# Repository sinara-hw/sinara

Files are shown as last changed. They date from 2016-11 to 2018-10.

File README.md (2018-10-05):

This repository is largely depreciated as we now give each piece of hardware its own repository within the [sinara-hw organization](https://github.com/sinara-hw) instead of using this one.

The main exception is issue tracking for Sayma which remains [here](https://github.com/sinara-hw/sinara/issues).

The [meta repository](https://github.com/sinara-hw/meta) is where Sinara management, inter-board design, incubation of new projects, etc. now occur.  Use either the [Main Sinara Wiki](https://github.com/sinara-hw/meta/wiki) or [Meta Issue Tracker](https://github.com/sinara-hw/meta/issues) as appropriate.

All work is licensed under CERN OHL v1.2.

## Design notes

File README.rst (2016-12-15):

Metlino
-------
- ARTIQ_EE/PCB_Metlino is Metlino board housing ARTIQ master FPGA (MCH Tongues 3,4)
- ARTIQ_ALTIUM/PCB_MCH_mordovia is a bare bones clock distribution board (MCH Tongue 2)
- NAT-MCH-Base12-GbE is a commercial MCH that acts as crate controller (MCH Tongue 1)
- these three cards are stacked and shared a common front panel

Sayma
-----
- ARTIQ_EE/PCB_Sayma_AMC is Sayma board with high speed digital components 
- ARTIQ_EE/PCB_Sayma_RTM is Sayma RTM board housing DACs and ADCs
- ARTIQ_ALTIUM/PCB_baikal is Signal/CLK ditribution board for RF-Backplane, slot is eRTM15  (Issue #78)
- ARTIQ_ALTIUM/PCB_mezzanine_clock is DAC clock generation mezzanine
- ARTIQ_ALTIUM/PCB_mezzanine_clock_template is simple test board and template for more complex clock mezzanines 
- ARTIQ_ALTIUM/PCB_mezzanine_analog_template is simple test board and template for more complex analog mezzanines 
- ARTIQ_ALTIUM/PCB_mezzanine_analog_allaki is analog mezzanine for base band output and DC-100 kHz input 

Note
----
- ARTIQ_EE folder is for designs made with the Mentor Graphics Xpedition Enterprise CAD tool.
- ARTIQ_ALTIUM folder is for designs made with Altium Designer CAD tool.
- See Issue 21_ for a list of hardware that comprises a Sinara system. 
.. _21: https://github.com/m-labs/sinara/issues/21

Modules to add to git
---------------------
- let ARTIQ_xx/BP_AMC/PCB_BP_AMC be microTCA.4 AMC backplane (no schematic currently available) 
- let ARTIQ_xx/BP_RTM/PCB_BP_RTM_RF be microTCA.4 RF backplane (no schematic currently available)

--------------
The hardware designs for the Sinara device family are distributed under the
CERN Open Hardware Licence v1.2.

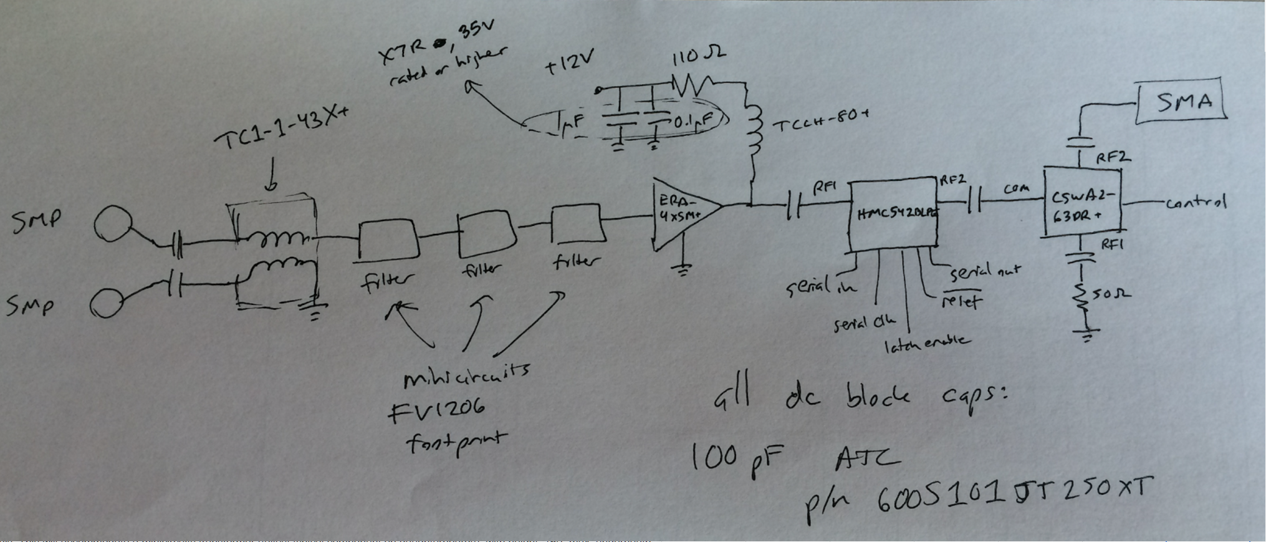
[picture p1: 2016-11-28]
ARTIQ_ALTIUM/Sayma_AFEs/BaseMod/Docs/paper_schematic.png

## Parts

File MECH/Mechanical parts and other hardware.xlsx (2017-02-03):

 | MFR |  | Sayma AMC | Sayma RTM | Metlino | Kasli | VHDCI BB | BNC IO | SMA IO | RJ45IO | DAC
LED lightpipes | BIVAR | PLPC1-100 | 6
AMC panel | Schroff | 21850070 | 1 | 1
MTCA panel | Schroff | 21850071 |  |  | 1
3U panel |  |  |  |  |  | 20848664 | 20848664 | 20849107 | 20848664 | 20848664 | 20848670
SMA isolation washer | http://www.rf-microwave.com/datasheets/603_Huber-Suhner_77-Z-0-0-8_01.pdf
AMC/Metlino heatsink | AAVID | 342947 (http://www.aavid.com/products/bga/342947) | 1 |  | 1
RTM/Kasli heatsink
RTM standoff 9mm M2.5 | RAF ELECTRONIC HARDWARE (http://pl.farnell.com/raf-electronic-hardware/m1256-2545-al/spacer-standoff-hex-aluminium/dp/1873361) | M1256-2545-AL (http://pl.farnell.com/raf-electronic-hardware/m1256-2545-al/spacer-standoff-hex-aluminium/dp/1873361) |  | 20
RTM standoff screw M2.5 6mm | DURATOOL (http://pl.farnell.com/duratool/m2-56-prstmcz100/screw-pozi-pan-steel-bzp-m2-5x6/dp/1420388) | M2.56 PRSTMCZ100- (http://pl.farnell.com/duratool/m2-56-prstmcz100/screw-pozi-pan-steel-bzp-m2-5x6/dp/1420388) |  | 40
SATA cable 1m |  |  | 1
SFP plug |  |  | 1
ATX supply |  |  |  |  | 1
IDC cable 30 wires |  |  |  |  |  |  | 1 | 1 | 1 | 2 | 1
IDC plug 30 contacts |  |  |  |  |  |  | 2 | 2 | 2 | 4 | 2
VHDCI cable |  |  |  |  | 2
FMC EMC strip for AMC |  |  | 1
12V wall wart |  |  |  |  |  | 1 | 1
SMA assembly distance |  |  |  | 8 | 2
SMP-SMP jack 6.45mm | Radiall | R222 705 000 |  | 48 |  |  |  |  |  |  |  | 7.6$@100
SMP-SMP jack 6.45mm | Rosenberger | 19K101-K00L5 |  |  |  |  |  |  |  |  |  | 8.09$@100
SMP-SMP jack 6.40mm | TE | 1056700-1
SMP-SMP jack 6.46 | Molex | 73415-4295 / 73415-4293
SMP-SMP jack 6.46 | Amphenol | 1290-4008 (http://www.digikey.com/product-detail/en/amphenol-sv-microwave/1290-4008/1290-4008-ND/6050843) |  |  |  |  |  |  |  |  |  | 15.8$@100
SMP-SMP jack 6.45 | Telegarthener | J01392A0001

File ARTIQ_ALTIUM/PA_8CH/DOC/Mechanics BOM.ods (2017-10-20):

Item name | description | quantity | remarks
20860-606 | modified Schroff enclosure | 1
PMD1207PTV1AF (https://www.tme.eu/pl/katalog/?art=PMD1207PTV1AF) | fan 70x70x25 | 5 | fan holes -> 5mm
STP5X10 (https://www.tme.eu/pl/details/stp5x10/elementy-montazowe/) | fan screw | 20
 | user module fixing | 1
 | mainboard platform | 1
 | RF module fixing | 1
7662686 | IEC inlet Schrack | 1
Threaded Strip M3, 30821-589, Pentair Schroff | threaded insert | 2
HLG-185H-30A (https://www.tme.eu/pl/details/hlg-185h-30a/zasilacze-do-led/mean-well/) | power supply module 30V/6A

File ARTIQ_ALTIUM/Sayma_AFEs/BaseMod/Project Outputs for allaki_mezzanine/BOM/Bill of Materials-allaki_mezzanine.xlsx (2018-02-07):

Comment | Description | Designator | Footprint | Manufacturer | Manufacturer Part Number | Manufacturer1 ComponentHeight | Manufacturer1 Example | Manufacturer1 Part Number | Part Description | Part Number | Quantity
100nF | Non-polarised capacitor | C1A, C1B, C5A, C5B, C6A, C6B, C22A, C22B, C35A, C35B, C40A, C40B, C41A, C41B, C43, C54, C57A, C57B, C58A, C58B, C59A, C59B, C60A, C60B | CAPC1005X55N | GENERIC | CC0402_100NF_16V_10%_X5R, CC0402_100NF_16V_10%_X5R, CC0402_100NF_16V_10%_X5R, CC0402_100NF_16V_10%_X5R, CC0402_100NF_16V_10%_X5R, CC0402_100NF_16V_10%_X5R, CC0402_100NF_16V_10%_X7R, CC0402_100NF_16V_10%_X7R, CC0402_100NF_16V_10%_X7R, CC0402_100NF_16V_10%_X7R, CC0402_100NF_16V_10%_X7R, CC0402_100NF_16V_10%_X7R, CC0402_100NF_16V_10%_X7R, CC0402_100NF_16V_10%_X7R, CC0402_100NF_16V_10%_X5R, CC0402_100NF_16V_10%_X5R, CC0402_100NF_16V_10%_X5R, CC0402_100NF_16V_10%_X5R, CC0402_100NF_16V_10%_X5R, CC0402_100NF_16V_10%_X5R, CC0402_100NF_16V_10%_X5R, CC0402_100NF_16V_10%_X5R, CC0402_100NF_16V_10%_X5R, CC0402_100NF_16V_10%_X5R | 0.55mm | MURATA | GRM155R61C104KA88D, GRM155R61C104KA88D, GRM155R61C104KA88D, GRM155R61C104KA88D, GRM155R61C104KA88D, GRM155R61C104KA88D, GRM155R71C104KA88D, GRM155R71C104KA88D, GRM155R71C104KA88D, GRM155R71C104KA88D, GRM155R71C104KA88D, GRM155R71C104KA88D, GRM155R71C104KA88D, GRM155R71C104KA88D, GRM155R61C104KA88D, GRM155R61C104KA88D, GRM155R61C104KA88D, GRM155R61C104KA88D, GRM155R61C104KA88D, GRM155R61C104KA88D, GRM155R61C104KA88D, GRM155R61C104KA88D, GRM155R61C104KA88D, GRM155R61C104KA88D | SMD Multilayer Chip Ceramic Capacitor | CC0402_100NF_16V_10%_X5R, CC0402_100NF_16V_10%_X5R, CC0402_100NF_16V_10%_X5R, CC0402_100NF_16V_10%_X5R, CC0402_100NF_16V_10%_X5R, CC0402_100NF_16V_10%_X5R, CC0402_100NF_16V_10%_X7R, CC0402_100NF_16V_10%_X7R, CC0402_100NF_16V_10%_X7R, CC0402_100NF_16V_10%_X7R, CC0402_100NF_16V_10%_X7R, CC0402_100NF_16V_10%_X7R, CC0402_100NF_16V_10%_X7R, CC0402_100NF_16V_10%_X7R, CC0402_100NF_16V_10%_X5R, CC0402_100NF_16V_10%_X5R, CC0402_100NF_16V_10%_X5R, CC0402_100NF_16V_10%_X5R, CC0402_100NF_16V_10%_X5R, CC0402_100NF_16V_10%_X5R, CC0402_100NF_16V_10%_X5R, CC0402_100NF_16V_10%_X5R, CC0402_100NF_16V_10%_X5R, CC0402_100NF_16V_10%_X5R | 24
10uF | Non-polarised capacitor | C2A, C2B, C7A, C7B, C11, C70 | CAPC1608X87N | GENERIC | CC0603_10uF_6.3V_20%_X5R | 0.95mm | KEMET | C0603C106M9PAC | SMD Multilayer Chip Ceramic Capacitor | CC0603_10UF_6.3V_20%_X5R | 6
1nF | Non-polarised capacitor | C3A, C3B, C8A, C8B, C23A, C23B | CAPC1005X55N | GENERIC | CC0402_1NF_50V_10%_X7R | 0.55mm | PHYCOMP | 223858715623 | SMD Multilayer Chip Ceramic Capacitor | CC0402_1NF_50V_10%_X7R | 6
10pF | Non-polarised capacitor | C4A, C4B, C63A, C63B | CAPC1608X87N | GENERIC | CC0603_10PF_50V_5%_NP0 | 0.87mm | PHYCOMP | 223886715109 | SMD Multilayer Chip Ceramic Capacitor | CC0603_10PF_50V_5%_NP0 | 4
18pF | Non-polarised capacitor | C9A, C9B, C33A, C33B | CAPC1005X55N | GENERIC | CC0402_18PF_50V_5%_C0G | 0.55mm | KEMET | C0402C180J5GACTU | SMD Multilayer Chip Ceramic Capacitor | CC0402_18PF_50V_5%_C0G | 4
10pF | Non-polarised capacitor | C10, C32 | CAPC1005X55N | GENERIC | CC0402_10PF_50V_5%_C0G | 0.55mm | KEMET | C0402C100J5GACTU | SMD Multilayer Chip Ceramic Capacitor | CC0402_10PF_50V_5%_C0G | 2
1uF | Non-polarised capacitor | C12A, C12B | CAPC2012X140N | GENERIC | CC0805_1UF_35V_20%_X7R | 1.35mm | TAIYO YUDEN | GMK212B7105MG-T | SMD Multilayer Chip Ceramic Capacitor | CC0805_1UF_35V_20%_X7R | 2
100nF | Non-polarised capacitor | C13A, C13B | CAPC1608X87N | GENERIC | CC0603_100NF_50V_10%_X7R | 0.87mm | PHYCOMP | 223858615649 | SMD Multilayer Chip Ceramic Capacitor | CC0603_100NF_50V_10%_X7R | 2
10nF | Non-polarised capacitor | C14A, C14B, C15A, C15B, C16A, C16B, C17A, C17B, C18A, C18B, C19A, C19B, C20A, C20B, C28A, C28B, C29A, C29B, C36A, C36B, C37A, C37B, C46A, C46B, C47A, C47B, C49A, C49B, C50A, C50B, C51, C52, C55A, C55B, C56A, C56B, C64, C65, C66, C67, C68, C69 | CAPC1005X55N | GENERIC | CC0402_10NF_16V_10%_X7R | 0.55mm | PHYCOMP | 223878715636 | SMD Multilayer Chip Ceramic Capacitor | CC0402_10NF_16V_10%_X7R | 42
10uF | Non-polarised capacitor | C21A, C21B, C39A, C39B | CAPC1608X80N | GENERIC | CC0603_10UF_16V_20%_X5R | 0.8mm | MURATA | GRM188R61C106MA73D | SMD Multilayer Chip Ceramic Capacitor | CC0603_10UF_16V_20%_X5R | 4
100pF | Non-polarised capacitor | C24A, C24B, C30A, C30B, C38A, C38B, C45A, C45B, C61A, C61B, C62A, C62B | CAPC1005X55N | GENERIC | CC0402_100PF_50V_5%_C0G | 0.55mm | KEMET | C0402C101J5GACTU | SMD Multilayer Chip Ceramic Capacitor | CC0402_100PF_50V_5%_C0G | 12
4.7uF | Non-polarised capacitor | C25, C26, C71, C72 | CAPC1709X95N | GENERIC | CC0603_4.7UF_16V_10%_X5R | 0.95mm | TAIYO YUDEN | EMK107ABJ475KA-T | SMD Multilayer Chip Ceramic Capacitor | CC0603_4.7UF_16V_10%_X5R | 4
2.2uF | Non-polarised capacitor | C27, C53 | CAPC1608X90N | GENERIC | CC0603_2.2UF_10V_20%_X7R | 0.9mm | TAIYO YUDEN | LMK107B7225MA-T | SMD Multilayer Chip Ceramic Capacitor | CC0603_2.2UF_10V_20%_X7R | 2
180pF | Non-polarised capacitor | C31A, C31B | CAPC3216X140N | GENERIC | CC1206_180PF_50V_5%_NP0 | 1.7mm | VISHAY VITRAMON | VJ1206A181JXAAT | SMD Multilayer Chip Ceramic Capacitor | CC1206_180PF_50V_5%_NP0 | 2
10uF | Polarised capacitor | C34A, C34B, C42A, C42B | CAPMP3216X180N | AVX | TCJA106M016R0200 |  |  |  | ESR 0R200 Tantalum Solid Electrolytic Chip Capacitor with Conductive Polymer Electrode | CTE3216-18_10UF_16V_20%_AVX_TCJ | 4
0.5pF | CAP 0.5pF 10V ±0.1pF 0402 (1005 Metric) Thickness 0.6mm SMD | C44A, C44B, C48A, C48B | CAPC0402(1005)60_M |  |  |  |  |  |  |  | 4
BAV199 | Serial Diode | D1A, D1B, D2A, D2B, D3A, D3B, D4A, D4B | SOT95P240X110-3N | NXP SEMICONDUCTORS | BAV199 |  |  |  | Low-Leakage Double Diode | BAV199 | 8
1PS76SB10 | Schottky Diode | D5, D6 | SOD2512X110N | NXP SEMICONDUCTORS | 1PS76SB10 |  |  |  | Schottky Barrier Single Diode | 1PS76SB10 | 2
DC to 3000MHz | 50 Ohm DC to 3000MHz Low Pass Filter | FL2A, FL2B, FL3A, FL3B, FL4A, FL4B | FIL_MINI-CIRCUITS_FV1206 | MINI-CIRCUITS | LFCN-3000+ |  |  |  | 50 Ohm Low Pass Filter | FIL_MINI-CIRCUITS_LFCN-3000+ | 6
ADT7420UCPZ-R2 | ±0.25°C Accurate, 16-Bit Digital I2C Temperature Sensor | IC1 | QFN65P400X400X80-17N-S270 | ANALOG DEVICES | ADT7420UCPZ-R2 |  |  |  | -20° to +105°C ±0.25°C Accurate, 16-Bit Digital I2C Temperature Sensor | ADT7420UCPZ-R2 | 1
ADA4927-1YCPZ-R2 | Ultralow Distortion Current Feedback Differential ADC Driver | IC2A, IC2B | QFN50P300X300X100-17N-S145 | ANALOG DEVICES | ADA4927-1YCPZ-R2 |  |  |  | Ultralow Distortion Current Feedback Differential ADC Driver | ADA4927-1YCPZ-R2 | 2
HMC542BLP4E | 0.5dB LSB GaAs MMIC 6-bit Digital Serial Control Attenuator, DC - 4GHz | IC3A, IC3B | QFN50P400X400X100-25N-S295 | HITTITE MICROWAVE CORP | HMC542BLP4E |  |  |  | 0.5dB LSB GaAs MMIC 6-bit Digital Serial Control Attenuator, DC to 4GHz | HMC542BLP4E | 2
YAT-12+ | DC to 18GHz, 2W, 50 Ohm, 4dB Attenuator | IC4A, IC4B | MINI-CIRCUITS_MC1630 | MINI-CIRCUITS | YAT-12+ |  |  |  | DC to 18GHz, 2W, 50 Ohms, 12dB Attenuator | YAT-12+ | 2
ERA-4XSM+ | DC-4GHz Monolithic Amplifier | IC5A, IC5B | MINI-CIRCUITS_WW107 | MINI-CIRCUITS | ERA-4XSM+ |  |  |  | DC-4GHz Monolithic Amplifier | ERA-4XSM+ | 2
AD8253ARMZ | 10MHz, 20V/us, G= 1, 10, 100, 1000 iCMOS Programmable Gain Instrumentation Amplifier | IC6A, IC6B | SOP50P490X110-10N | ANALOG DEVICES | AD8253ARMZ |  |  |  | 10MHz, 20V/us, G= 1, 10, 100, 1000 iCMOS Programmable Gain Instrumentation Amplifier | AD8253ARMZ | 2
HMC349ALP4CE | DC-4GHz High Isolation SPDT Non-Reflective Switch | IC7A, IC7B | QFN65P400X400X100-17N-S255 | ANALOG DEVICES | HMC349ALP4CE |  |  |  | DC-4GHz High Isolation SPDT Non-Reflective Switch | HMC349ALP4CE | 2
LT3045EDD#PBF | 20V, 500mA, Ultralow Noise, Ultrahigh PSRR Linear Regulator | IC8, IC10 | SON50P300X300X80-11N-R175X248 | LINEAR TECHNOLOGY | LT3045EDD#PBF |  |  |  | 20V, 500mA, Ultralow Noise, Ultrahigh PSRR Linear Regulator | LT3045EDD#PBF | 2
ADP7182AUJZ-5.0-R7 | –5V, 200 mA, Low Noise, Linear Regulator | IC9 | SOT95P280X90-5N | ANALOG DEVICES | ADP7182AUJZ-5.0-R7 |  |  |  | –5V, -200mA, Low Noise, Linear Regulator | ADP7182AUJZ-5.0-R7 | 1
24AA02E48T-I/OT | 1.7V-5.5V, 2K I2C Serial EEPROM With EUI-48 Node Identity | IC14 | SOT95P280X145-5N | MICROCHIP TECHNOLOGY | 24AA02E48T-I/OT |  |  |  | 1.7V-5.5V, 2K I2C Serial EEPROM With EUI-48 Node Identity | 24AA02E48T-I/OT | 1
SMP | 50 Ohms, SMP Surface/THT Mount Plug, Limited Detent | J1, J3, J4, J6, J14, J15 | AMPHENOL_SMP-MSLD-PCT-10 | AMPHENOL | SMP-MSLD-PCT-10 |  |  |  | 50 Ohms, SMP Surface Mount Plug, Limited Detent | AMPHENOL_SMP-MSLD-PCT-10 | 6
SMA | RiSMA 50 Ohms Right Angle PCB Jack | J2, J5 | Telegartner_J01151A0921 | Telegartner | J01151A0921 |  |  |  | SMA 50 Ohms Right Angle PCB Jack | Telegartner_J01151A0921 | 2
SMP |  | J7, J9, J10, J12 | MOLEX_85305-0232 | MOLEX | 85305-0232 |  |  |  | 50 Ohms, SMP Surface Mount Plug, Limited Detent | MOLEX_85305-0232 | 4
SMA |  | J8, J11 | TELEGARTNER_J01151A0451 | TELEGARTNER | J01151A0451 |  |  |  | SMA 50 ohms Edge Mount Bulkhead Jack Receptacle | TELEGARTNER_J01151A0451 | 2
Familly | 40 Contacts, Pitch 0.635mm, Razor Beam LSS Vertical High Speed Hermaphroditic Strip (Lead Style 7.49mm) | J13 | SAMTEC_LSS-120-02-L-DV-A | SAMTEC | LSS-120-02-L-DV-A |  |  |  | 40 Contacts, Pitch 0.635mm, Razor Beam LSS Vertical High Speed Hermaphroditic Strip (Lead Style 5.49mm) | SAMTEC_LSS-120-02-L-DV-A | 1
0.5uH@200mA | 50 Ohms, 50 to 8200 MHz RF Choke | L1A, L1B | IND_MINI-CIRCUITS_GU1604 | MINI-CIRCUITS | TCCH-80+ |  |  |  | 50 Ohms, 50 to 8200 MHz RF Choke | IND_MINI-CIRCUITS_TCCH-80+ | 2
390R@100MHz | Inductor | L2A, L2B, L3A, L3B, L4, L5A, L5B, L6A, L6B, L7A, L7B, L8A, L8B, L9, L10 | INDC1608X95N | TDK | MPZ1608R391A |  |  |  | SMT Chip Bead for Power Line | IND0603_TDK_MPZ1608R391A | 15
698 | Resistor - 0.1% | R1A, R1B, R9A, R9B, R13A, R13B, R22A, R22B | RESC1608X55N | GENERIC | R0603_698R_0.1%_0.063W_10PPM | 0.5mm | TYCO HOLSWORTHY | RN73C1J698RBTDF | Thin Film Chip Resistor | R0603_698R_0.1%_0.063W_10PPM | 8
0 | Resistor | R2A, R2B, R3A, R3B, R4A, R4B, R7A, R7B, R10A, R10B, R14A, R14B, R15A, R15B, R21A, R21B, R24A, R24B, R35A, R35B, R38A, R38B, R43A, R43B, R44A, R44B, R45A, R45B, R46A, R46B, R47A, R47B, R48A, R48B, R49A, R49B, R50A, R50B, R51A, R51B, R52A, R52B, R53A, R53B, R54A, R54B, R55A, R55B, R56A, R56B, R57A, R57B, R58A, R58B, R59A, R59B, R65A, R65B, R66A, R66B, R67A, R67B | RESC1005X40N | GENERIC | R0402_0R_JUMPER | 0.4mm | YAGEO PHYCOMP | 232270591001L | 1A (0.05R Max DC Resistance) Zero Ohm Jumper | R0402_0R_JUMPER | 62
100 | Resistor - 1% | R5A, R5B | RESC3216X65N | GENERIC | R1206_100R_1%_0.25W_100PPM | 0.65mm | NIC COMPONENT | NRC12F4700TRF | General Purpose Thick Film Chip Resistor | R1206_100R_1%_0.25W_100PPM | 2
DNP | Resistor, Resistor, Resistor, Resistor, Resistor, Resistor, Resistor, Resistor, Resistor - 1%, Resistor - 1% | R6A, R6B, R8A, R8B, R11A, R11B, R12A, R12B, R16A, R16B | RESC1005X40N | GENERIC | R0402_0R_JUMPER, R0402_0R_JUMPER, R0402_0R_JUMPER, R0402_0R_JUMPER, R0402_0R_JUMPER, R0402_0R_JUMPER, R0402_0R_JUMPER, R0402_0R_JUMPER, R0402_56R_1%_0.0625W_100PPM, R0402_56R_1%_0.0625W_100PPM | 0.4mm | YAGEO PHYCOMP | 232270591001L, 232270591001L, 232270591001L, 232270591001L, 232270591001L, 232270591001L, 232270591001L, 232270591001L, 232270675609L, 232270675609L | 1A (0.05R Max DC Resistance) Zero Ohm Jumper, 1A (0.05R Max DC Resistance) Zero Ohm Jumper, 1A (0.05R Max DC Resistance) Zero Ohm Jumper, 1A (0.05R Max DC Resistance) Zero Ohm Jumper, 1A (0.05R Max DC Resistance) Zero Ohm Jumper, 1A (0.05R Max DC Resistance) Zero Ohm Jumper, 1A (0.05R Max DC Resistance) Zero Ohm Jumper, 1A (0.05R Max DC Resistance) Zero Ohm Jumper, General Purpose Thick Film Chip Resistor, General Purpose Thick Film Chip Resistor | R0402_0R_JUMPER, R0402_0R_JUMPER, R0402_0R_JUMPER, R0402_0R_JUMPER, R0402_0R_JUMPER, R0402_0R_JUMPER, R0402_0R_JUMPER, R0402_0R_JUMPER, R0402_56R_1%_0.0625W_100PPM, R0402_56R_1%_0.0625W_100PPM | 10
100 | Resistor - 1% | R17 | RESC1005X40N | GENERIC | R0402_100R_1%_0.0625W_100PPM | 0.4mm | YAGEO PHYCOMP | 232270671001L | General Purpose Thick Film Chip Resistor | R0402_100R_1%_0.0625W_100PPM | 1
100 | Resistor - 1% | R18A, R18B, R19A, R19B | RESC0603X28N | GENERIC | R0201_100R_1%_0.05W_200PPM | 0.27mm | VISHAY | CRCW0201100RFNED | Thick Film Chip Resistor | R0201_100R_1%_0.05W_200PPM | 4
4k7 | Resistor - 1% | R20A, R20B, R23A, R23B | RESC1005X40N | GENERIC | R0402_4K7_1%_0.0625W_100PPM | 0.4mm | YAGEO PHYCOMP | 232270674702L | General Purpose Thick Film Chip Resistor | R0402_4K7_1%_0.0625W_100PPM | 4
1k4 | Resistor - 0.1% | R25A, R25B | RESC1608X55N | GENERIC | R0603_1K4_0.1%_0.063W_10PPM | 0.5mm | TYCO HOLSWORTHY | RN73C1J1K4BTDF | Thin Film Chip Resistor | R0603_1K4_0.1%_0.063W_10PPM | 2
1k | Resistor - 1% | R26A, R26B, R27A, R27B, R31A, R31B, R41A, R41B | RESC1005X40N | GENERIC | R0402_1K_1%_0.0625W_100PPM | 0.4mm | YAGEO PHYCOMP | 232270671002L | General Purpose Thick Film Chip Resistor | R0402_1K_1%_0.0625W_100PPM | 8
845 | Resistor - 0.1% | R28A, R28B | RESC1608X55N | GENERIC | R0603_845R_0.1%_0.063W_10PPM | 0.5mm | TYCO HOLSWORTHY | RN73C1J845RBTDF | Thin Film Chip Resistor | R0603_845R_0.1%_0.063W_10PPM | 2
3k24 | Resistor - 0.1% | R29A, R29B | RESC1608X55N | GENERIC | R0603_3K24_0.1%_0.063W_10PPM | 0.5mm | TYCO HOLSWORTHY | RN73C1J3K24BTDF | Thin Film Chip Resistor | R0603_3K24_0.1%_0.063W_10PPM | 2
13k | Resistor - 1% | R30A, R30B | RESC1005X40N | GENERIC | R0402_13K_1%_0.0625W_100PPM | 0.4mm | YAGEO PHYCOMP | 232270671303L | General Purpose Thick Film Chip Resistor | R0402_13K_1%_0.0625W_100PPM | 2
10k | Resistor - 1% | R32A, R32B | RESC1005X40N | GENERIC | R0402_10K_1%_0.0625W_100PPM | 0.4mm | YAGEO PHYCOMP | 232270671003L | General Purpose Thick Film Chip Resistor | R0402_10K_1%_0.0625W_100PPM | 2
1k5 | Resistor - 0.1% | R33A, R33B, R36A, R36B | RESC1608X55N | GENERIC | R0603_1K5_0.1%_0.063W_10PPM | 0.5mm | TYCO HOLSWORTHY | RN73C1J1K5BTDF | Thin Film Chip Resistor | R0603_1K5_0.1%_0.063W_10PPM | 4
100k | Resistor - 0.1% | R34A, R34B, R37A, R37B | RESC1005X35N | GENERIC | R0402_100K_0.1%_0.063W_25PPM | 0.35mm | TE CONNECTIVITY | CPF0402B100KE1 | Thin Film Precision Resistor | R0402_100K_0.1%_0.063W_25PPM | 4
49k9 | Resistor - 0.1% | R39 | RESC1608X55N | GENERIC | R0603_49K9_0.1%_0.063W_10PPM | 0.5mm | TYCO HOLSWORTHY | RN73C1J49K9BTDF | Thin Film Chip Resistor | R0603_49K9_0.1%_0.063W_10PPM | 1
49R9 | Resistor - 1% | R40A, R40B, R42A, R42B | RESC1005X40N | GENERIC | R0402_49R9_1%_0.0625W_100PPM | 0.4mm | YAGEO PHYCOMP | 232270674999L or RC0402FR-0749R9L | General Purpose Thick Film Chip Resistor | R0402_49R9_1%_0.0625W_100PPM | 4
115k | Resistor - 0.1% | R60 | RESC1608X55N | GENERIC | R0603_115K_0.1%_0.063W_10PPM | 0.5mm | TYCO HOLSWORTHY | RN73C1J115KBTDF | Thin Film Chip Resistor | R0603_115K_0.1%_0.063W_10PPM | 1
100k | Resistor - 1% | R61, R62, R63, R64 | RESC1005X40N | GENERIC | R0402_100K_1%_0.0625W_100PPM | 0.4mm | YAGEO PHYCOMP | 232270671004L | General Purpose Thick Film Chip Resistor | R0402_100K_1%_0.0625W_100PPM | 4
3k3 | Resistor - 1% | R68A, R68B | RESC1005X40N | GENERIC | R0402_3K3_1%_0.0625W_100PPM | 0.4mm | YAGEO PHYCOMP | 232270673302L | General Purpose Thick Film Chip Resistor | R0402_3K3_1%_0.0625W_100PPM | 2
1:2 | 50 OHMS 10 to 4000 MHz RF Transformer | TR1A, TR1B | XFMR_MINI-CIRCUITS_DB1627 | MINI-CIRCUITS | TCM2-43X+ |  |  |  | 50 Ohms 10 to 4000MHz RF Transformer | XFMR_MINI-CIRCUITS_TCM2-43X+ | 2
AD8363ACPZ-WP | 50 Hz to 6 GHz,50 dB TruPwr™ Detector, 3µs Response Time, CP-16-10, Pb-Free, 64 Tray | U1A, U1B | ADI-CP-16-10_M |  |  |  |  |  |  |  | 2

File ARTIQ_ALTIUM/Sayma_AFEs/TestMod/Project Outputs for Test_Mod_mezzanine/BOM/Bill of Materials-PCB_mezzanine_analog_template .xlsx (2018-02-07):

Comment | Description | Designator | Footprint | Manufacturer | Manufacturer Part Number | Manufacturer1 ComponentHeight | Manufacturer1 Example | Manufacturer1 Part Number | Part Description | Part Number | Quantity
100nF | Non-polarised capacitor | C1A, C1B, C5A, C5B, C6A, C6B, C7A, C7B, C10, C12 | CAPC1005X55N | GENERIC | CC0402_100NF_16V_10%_X5R | 0.55mm | MURATA | GRM155R61C104KA88D | SMD Multilayer Chip Ceramic Capacitor | CC0402_100NF_16V_10%_X5R | 10
10uF | Non-polarised capacitor | C2A, C2B, C8A, C8B | CAPC1608X87N | GENERIC | CC0603_10uF_6.3V_20%_X5R | 0.95mm | KEMET | C0603C106M9PAC | SMD Multilayer Chip Ceramic Capacitor | CC0603_10UF_6.3V_20%_X5R | 4
1nF | Non-polarised capacitor | C3A, C3B, C9A, C9B | CAPC1005X55N | GENERIC | CC0402_1NF_50V_10%_X7R | 0.55mm | PHYCOMP | 223858715623 | SMD Multilayer Chip Ceramic Capacitor | CC0402_1NF_50V_10%_X7R | 4
10pF | Non-polarised capacitor | C4A, C4B | CAPC1608X87N | GENERIC | CC0603_10PF_50V_5%_NP0 | 0.87mm | PHYCOMP | 223886715109 | SMD Multilayer Chip Ceramic Capacitor | CC0603_10PF_50V_5%_NP0 | 2
1uF | Non-polarised capacitor | C11, C25, C26, C27 | CAPC2012X140N | GENERIC | CC0805_1UF_35V_20%_X7R | 1.35mm | TAIYO YUDEN | GMK212B7105MG-T | SMD Multilayer Chip Ceramic Capacitor | CC0805_1UF_35V_20%_X7R | 4
100nF | Non-polarised capacitor | C13A, C13B | CAPC1608X87N | GENERIC | CC0603_100NF_50V_10%_X7R | 0.87mm | PHYCOMP | 223858615649 | SMD Multilayer Chip Ceramic Capacitor | CC0603_100NF_50V_10%_X7R | 2
Use only in PCB | Fiducial Target | FTG1 | FIDUCIAL_TOP_C100-200 |  |  |  |  |  | Round Fiducial Target, Top Layer, 1.0mm, Top Solder 2.0mm, Keepout =2.0mm | FIDUCIAL_TARGET_C100-200 | 1
Use only in PCB | Fiducial Target | FTG2, FTG3 | FIDUCIAL_TOP_S100-200 |  |  |  |  |  | Square Fiducial Target, Top Layer, 1.0mm, Top Solder 2.0mm, Keepout =2.0mm | FIDUCIAL_TARGET_S100-200 | 2
Use only in PCB | Fiducial Target | FTG4 | FIDUCIAL_TOP_S200-400 |  |  |  |  |  | Square Fiducial Target, Top Layer, 2.0mm, Top Solder 4.0mm, Keepout =4.0mm | FIDUCIAL_TARGET_S200-400 | 1
TCA9539RTWR | Low-Voltage 16-Bit I2C and SMBus I/O Expander | IC1, IC5 | QFN50P400X400X80-25N-S255 | TEXAS INSTRUMENTS | TCA9539RTWR |  |  |  | Low Voltage 16-Bit I2C and SMBus Low-Power I/O Expander With Interrupt Output, Reset Pin, Configuration Registers | TCA9539RTWR | 2
ADA4927-1YCPZ-R2 | Ultralow Distortion Current Feedback Differential ADC Driver | IC2A, IC2B | QFN50P300X300X100-17N-S145 | ANALOG DEVICES | ADA4927-1YCPZ-R2 |  |  |  | Ultralow Distortion Current Feedback Differential ADC Driver | ADA4927-1YCPZ-R2 | 2
24AA02E48T-I/OT | 1.7V-5.5V, 2K I2C Serial EEPROM With EUI-48 Node Identity | IC3 | SOT95P280X145-5N | MICROCHIP TECHNOLOGY | 24AA02E48T-I/OT |  |  |  | 1.7V-5.5V, 2K I2C Serial EEPROM With EUI-48 Node Identity | 24AA02E48T-I/OT | 1
LM75AIMM/NOPB | Digital Temperature Sensor and Thermal Watchdog with Two-Wire Interface | IC4 | SOP65P490X109-8N | TEXAS INSTRUMENTS | LM75AIMM/NOPB |  |  |  | -25° to +100°C ±2°C Digital Temperature Sensor and Thermal Watchdog with Two-Wire Interface | LM75AIMM/NOPB | 1
ADP7102ARDZ-5.0-R7 | 300 mA, Low Noise, CMOS LDO Linear Regulator | IC6 | SOIC127P600X175-9N-R241X309 | ANALOG DEVICES | ADP7102ARDZ-5.0-R7 |  |  |  | 5V, 300mA, Low Noise, CMOS LDO Linear Regulator | ADP7102ARDZ-5.0-R7 | 1
ADP7182AUJZ-5.0-R7 | –5V, 200 mA, Low Noise, Linear Regulator | IC7 | SOT95P280X90-5N | ANALOG DEVICES | ADP7182AUJZ-5.0-R7 |  |  |  | –5V, -200mA, Low Noise, Linear Regulator | ADP7182AUJZ-5.0-R7 | 1
SMP |  | J7, J9, J10, J12 | MOLEX_85305-0232 | MOLEX | 85305-0232 |  |  |  | 50 Ohms, SMP Surface Mount Plug, Limited Detent | MOLEX_85305-0232 | 4
SMA |  | J8, J11 | TELEGARTNER_J01151A0451 | TELEGARTNER | J01151A0451 |  |  |  | SMA 50 ohms Edge Mount Bulkhead Jack Receptacle | TELEGARTNER_J01151A0451 | 2
Familly | 40 Contacts, Pitch 0.635mm, Razor Beam LSS Vertical High Speed Hermaphroditic Strip (Lead Style 7.49mm) | J13 | SAMTEC_LSS-120-02-L-DV-A | SAMTEC | LSS-120-02-L-DV-A |  |  |  | 40 Contacts, Pitch 0.635mm, Razor Beam LSS Vertical High Speed Hermaphroditic Strip (Lead Style 5.49mm) | SAMTEC_LSS-120-02-L-DV-A | 1
SMP |  | J16, J18, J19, J21, J22, J23 | AMPHENOL_SMP-MSLD-PCT-10 | AMPHENOL | SMP-MSLD-PCT-10 |  |  |  | 50 Ohm RF Connector, SMP Straight PCB Jack, Limited Detent, Surface Mount with Thru-Hole Contact | AMPHENOL_SMP-MSLD-PCT-10 | 6
SMA |  | J17, J20 | TELEGARTNER_J01151A0921 | TELEGARTNER | J01151A0921 |  |  |  | 50 Ohm SMA Right Angle PCB Jack | TELEGARTNER_J01151A0921 | 2
10k | Resistor - 1% | R1, R2, R7, R8, R44, R45, R46, R47, R48, R49, R50, R51, R52, R53, R54, R55 | RESC1005X40N | GENERIC | R0402_10K_1%_0.0625W_100PPM | 0.4mm | YAGEO PHYCOMP | 232270671003L | General Purpose Thick Film Chip Resistor | R0402_10K_1%_0.0625W_100PPM | 16
1k | Resistor - 1% | R3, R4, R5, R6 | RESC1005X40N | GENERIC | R0402_1K_1%_0.0625W_100PPM | 0.4mm | YAGEO PHYCOMP | 232270671002L | General Purpose Thick Film Chip Resistor | R0402_1K_1%_0.0625W_100PPM | 4
332 | Resistor - 0.1% | R9A, R9B, R10A, R10B, R12A, R12B, R15A, R15B | RESC1608X55N | GENERIC | R0603_332R_0.1%_0.063W_10PPM | 0.5mm | TYCO HOLSWORTHY | RN73C1J332RBTDF | Thin Film Chip Resistor | R0603_332R_0.1%_0.063W_10PPM | 8
49R9 | Resistor - 1% | R11A, R11B, R14A, R14B | RESC1005X40N | GENERIC | R0402_49R9_1%_0.0625W_100PPM | 0.4mm | YAGEO PHYCOMP | 232270674999L or RC0402FR-0749R9L | General Purpose Thick Film Chip Resistor | R0402_49R9_1%_0.0625W_100PPM | 4
56 | Resistor - 1% | R13A, R13B, R16A, R16B | RESC1005X40N | GENERIC | R0402_56R_1%_0.0625W_100PPM | 0.4mm | YAGEO PHYCOMP | 232270675609L | General Purpose Thick Film Chip Resistor | R0402_56R_1%_0.0625W_100PPM | 4
100 | Resistor - 1% | R17 | RESC1005X40N | GENERIC | R0402_100R_1%_0.0625W_100PPM | 0.4mm | YAGEO PHYCOMP | 232270671001L | General Purpose Thick Film Chip Resistor | R0402_100R_1%_0.0625W_100PPM | 1
56 | Resistor - 5% | R18, R19, R21, R22 | RESC6331X70N | GENERIC | R2512_56R_5%_1W_200PPM | 0.7mm | TYCO ELECTRONICS | 352056RJT | Surface Mount Power Resistor | R2512_56R_5%_1W_200PPM | 4
8R2 | Resistor - 1% | R20, R23 | RESC3216X65N | GENERIC | R1206_8R2_1%_0.25W_200PPM | 0.65mm | PHYCOMP | 232272468208 | General Purpose Thick Film Chip Resistor | R1206_8R2_1%_0.25W_200PPM | 2
120 | Resistor - 1% | R24, R25, R26, R27 | RESC3216X65N | GENERIC | R1206_120R_1%_0.25W_100PPM | 0.65mm | NIC COMPONENT | NRC12F1200TRF | General Purpose Thick Film Chip Resistor | R1206_120R_1%_0.25W_100PPM | 4
2 | Resistor - 1% | R28, R29, R30, R31, R32, R33, R34, R35 | RESM11670X449N | VISHAY DALE | WSC45272R000FEA |  |  |  | Surface Mount Precision Power Wirewound Resistor | R4527_2R_1%_2W_50PPM | 8
62 | Resistor - 1% | R36, R37, R38, R39 | RESC3216X65N | GENERIC | R1206_62R_1%_0.25W_100PPM | 0.65mm | NIC COMPONENT | NRC12F62R0TRF | General Purpose Thick Film Chip Resistor | R1206_62R_1%_0.25W_100PPM | 4
3R3 | Resistor - 1% | R40, R41, R42, R43 | RESC6331X70N | GENERIC | R2512_3R3_1%_1W_200PPM | 0.65mm | YAGEO PHYCOMP | 232276363308L or RC2512FK-073R3L | Thick Film Chip Resistor | R2512_3R3_1%_1W_200PPM | 4
Switch | 2 Ways SPST DIP Switch | SW1 | SW_OMRON_A6S-2102-H | OMRON | A6S-2102-H |  |  |  | 2 Ways SPST DIP Switch, White Flat Actuator with Seal Tape, Contact Rating 25mA 24VDC | SW_OMRON_A6S-2102-H | 1
Switch | 8 Ways SPST DIP Switch | SW2 | SW_OMRON_A6S-8102-H | OMRON | A6S-8102-H |  |  |  | 8 Ways SPST DIP Switch, White Flat Actuator with Seal Tape, Contact Rating 25mA 24VDC | SW_OMRON_A6S-8102-H | 1
IRLML6402PBF | P-CHANNEL MOSFET WITH ZENER DIODE | T1, T2, T3, T4 | SOT95P237X112-3N | INTERNATIONAL RECTIFIER | IRLML6402PBF |  |  |  | -20V -3.7A P-Channel HEXFET® Power MOSFET | IRLML6402PBF | 4
DMN2020LSN-7 | 20V, 6.9A, N-Channel Enhancement Mode MOSFET | T5, T6, T7, T8, T9, T10, T11, T12 | SOT95P285X140-3N | DIODES INCORPORATED | DMN2020LSN-7 |  |  |  | 20V, 6.9A, N-Channel Enhancement Mode MOSFET | DMN2020LSN-7 | 8
Test Point | Test Point | TP1, TP2, TP3, TP4, TP5 | TPS127 |  |  |  |  |  | 1.27mm x 1.27mm PCB Copper Area (SMD Test Point) | SMD_PAD_1.27X1.27MM | 5
1:1 | 50 Ohms 4.5 To 3000MHz RF Transformers | TR1A, TR1B | XFMR_MINI-CIRCUITS_AT224 | MINI-CIRCUITS | TC1-1-13M+ |  |  |  | 50 Ohms 4.5 To 3000MHz RF Transformer | XFMR_MINI-CIRCUITS_TC1-1-13M+ | 2

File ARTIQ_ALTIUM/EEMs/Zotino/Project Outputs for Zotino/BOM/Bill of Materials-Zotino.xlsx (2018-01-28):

Comment | Description | Designator | Footprint | Manufacturer | Manufacturer Part Number | Manufacturer1 ComponentHeight | Manufacturer1 Example | Manufacturer1 Part Number | Part Description | Part Number | Quantity
Plated Hole | Single Terminal Socket | B2, B3, B4, B8, B9, B10 | c130h80 |  |  |  |  |  | Plated Through Hole: Hole Dia.=0.8mm Pad Dia.=1.3mm, IPC-7251 Level C | PLATED_HOLE0.8_PAD1.3 | 6
Plated Hole | Single Terminal Socket | B5, B6 | c160h110 |  |  |  |  |  | Plated Through Hole: Hole Dia.=1.1mm Pad Dia.=1.6mm, IPC-7251 Level C | PLATED_HOLE1.1_PAD1.6 | 2
10uF | Polarised capacitor | C1, C2, C3, C7, C10, C12, C14, C47, C79, C90_1, C90_2, C90_3, C90_4, C90_5, C90_6, C90_7, C90_8, C90_9, C90_10, C90_11, C90_12, C90_13, C90_14, C90_15, C90_16, C90_17, C90_18, C90_19, C90_20, C90_21, C90_22, C90_23, C90_24, C90_25, C90_26, C90_27, C90_28, C90_29, C90_30, C90_31, C90_32, C93_1, C93_2, C93_3, C93_4, C93_5, C93_6, C93_7, C93_8, C93_9, C93_10, C93_11, C93_12, C93_13, C93_14, C93_15, C93_16, C93_17, C93_18, C93_19, C93_20, C93_21, C93_22, C93_23, C93_24, C93_25, C93_26, C93_27, C93_28, C93_29, C93_30, C93_31, C93_32, C124, C132, C134, C136, C147 | CAPMP3216X180N | AVX | TCJA106M016R0200 |  |  |  | ESR 0R200 Tantalum Solid Electrolytic Chip Capacitor with Conductive Polymer Electrode | CTE3216-18_10UF_16V_20%_AVX_TCJ | 78
100nF | Non-polarised capacitor | C4, C5, C9, C13, C19, C20, C21, C22, C23, C24, C31, C33, C38, C50, C53, C69, C70, C78, C83, C91_1, C91_2, C91_3, C91_4, C91_5, C91_6, C91_7, C91_8, C91_9, C91_10, C91_11, C91_12, C91_13, C91_14, C91_15, C91_16, C91_17, C91_18, C91_19, C91_20, C91_21, C91_22, C91_23, C91_24, C91_25, C91_26, C91_27, C91_28, C91_29, C91_30, C91_31, C91_32, C92_1, C92_2, C92_3, C92_4, C92_5, C92_6, C92_7, C92_8, C92_9, C92_10, C92_11, C92_12, C92_13, C92_14, C92_15, C92_16, C92_17, C92_18, C92_19, C92_20, C92_21, C92_22, C92_23, C92_24, C92_25, C92_26, C92_27, C92_28, C92_29, C92_30, C92_31, C92_32, C148, C150 | CAPC1005X55N | GENERIC | CC0402_100NF_16V_10%_X5R, CC0402_100NF_16V_10%_X5R, CC0402_100NF_16V_10%_X7R, CC0402_100NF_16V_10%_X7R, CC0402_100NF_16V_10%_X5R, CC0402_100NF_16V_10%_X5R, CC0402_100NF_16V_10%_X5R, CC0402_100NF_16V_10%_X5R, CC0402_100NF_16V_10%_X5R, CC0402_100NF_16V_10%_X5R, CC0402_100NF_16V_10%_X7R, CC0402_100NF_16V_10%_X7R, CC0402_100NF_16V_10%_X5R, CC0402_100NF_16V_10%_X7R, CC0402_100NF_16V_10%_X7R, CC0402_100NF_16V_10%_X5R, CC0402_100NF_16V_10%_X5R, CC0402_100NF_16V_10%_X7R, CC0402_100NF_16V_10%_X7R, CC0402_100NF_16V_10%_X7R, CC0402_100NF_16V_10%_X7R, CC0402_100NF_16V_10%_X7R, CC0402_100NF_16V_10%_X7R, CC0402_100NF_16V_10%_X7R, CC0402_100NF_16V_10%_X7R, CC0402_100NF_16V_10%_X7R, CC0402_100NF_16V_10%_X7R, CC0402_100NF_16V_10%_X7R, CC0402_100NF_16V_10%_X7R, CC0402_100NF_16V_10%_X7R, CC0402_100NF_16V_10%_X7R, CC0402_100NF_16V_10%_X7R, CC0402_100NF_16V_10%_X7R, CC0402_100NF_16V_10%_X7R, CC0402_100NF_16V_10%_X7R, CC0402_100NF_16V_10%_X7R, CC0402_100NF_16V_10%_X7R, CC0402_100NF_16V_10%_X7R, CC0402_100NF_16V_10%_X7R, CC0402_100NF_16V_10%_X7R, CC0402_100NF_16V_10%_X7R, CC0402_100NF_16V_10%_X7R, CC0402_100NF_16V_10%_X7R, CC0402_100NF_16V_10%_X7R, CC0402_100NF_16V_10%_X7R, CC0402_100NF_16V_10%_X7R, CC0402_100NF_16V_10%_X7R, CC0402_100NF_16V_10%_X7R, CC0402_100NF_16V_10%_X7R, CC0402_100NF_16V_10%_X7R, CC0402_100NF_16V_10%_X7R, CC0402_100NF_16V_10%_X7R, CC0402_100NF_16V_10%_X7R, CC0402_100NF_16V_10%_X7R, CC0402_100NF_16V_10%_X7R, CC0402_100NF_16V_10%_X7R, CC0402_100NF_16V_10%_X7R, CC0402_100NF_16V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 | 0.55mm | MURATA | GRM155R61C104KA88D, GRM155R61C104KA88D, GRM155R71C104KA88D, GRM155R71C104KA88D, GRM155R61C104KA88D, GRM155R61C104KA88D, GRM155R61C104KA88D, GRM155R61C104KA88D, GRM155R61C104KA88D, GRM155R61C104KA88D, GRM155R71C104KA88D, GRM155R71C104KA88D, GRM155R61C104KA88D, GRM155R71C104KA88D, GRM155R71C104KA88D, GRM155R61C104KA88D, GRM155R61C104KA88D, GRM155R71C104KA88D, GRM155R71C104KA88D, GRM155R71C104KA88D, GRM155R71C104KA88D, GRM155R71C104KA88D, GRM155R71C104KA88D, GRM155R71C104KA88D, GRM155R71C104KA88D, GRM155R71C104KA88D, GRM155R71C104KA88D, GRM155R71C104KA88D, GRM155R71C104KA88D, GRM155R71C104KA88D, GRM155R71C104KA88D, GRM155R71C104KA88D, GRM155R71C104KA88D, GRM155R71C104KA88D, GRM155R71C104KA88D, GRM155R71C104KA88D, GRM155R71C104KA88D, GRM155R71C104KA88D, GRM155R71C104KA88D, GRM155R71C104KA88D, GRM155R71C104KA88D, GRM155R71C104KA88D, GRM155R71C104KA88D, GRM155R71C104KA88D, GRM155R71C104KA88D, GRM155R71C104KA88D, GRM155R71C104KA88D, GRM155R71C104KA88D, GRM155R71C104KA88D, GRM155R71C104KA88D, GRM155R71C104KA88D, GRM155R71C104KA88D, GRM155R71C104KA88D, GRM155R71C104KA88D, GRM155R71C104KA88D, GRM155R71C104KA88D, GRM155R71C104KA88D, GRM155R71C104KA88D, GRM155R71C104KA88D, GRM155R71C104KA88D, GRM155R71C104KA88D, GRM155R71C104KA88D, GRM155R71C104KA88D, GRM155R71C104KA88D, GRM155R71C104KA88D, GRM155R71C104KA88D, GRM155R71C104KA88D, GRM155R71C104KA88D, GRM155R71C104KA88D, GRM155R71C104KA88D, GRM155R71C104KA88D, GRM155R71C104KA88D, GRM155R71C104KA88D, GRM155R71C104KA88D, GRM155R71C104KA88D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 | SMD Multilayer Chip Ceramic Capacitor | CC0402_100NF_16V_10%_X5R, CC0402_100NF_16V_10%_X5R, CC0402_100NF_16V_10%_X7R, CC0402_100NF_16V_10%_X7R, CC0402_100NF_16V_10%_X5R, CC0402_100NF_16V_10%_X5R, CC0402_100NF_16V_10%_X5R, CC0402_100NF_16V_10%_X5R, CC0402_100NF_16V_10%_X5R, CC0402_100NF_16V_10%_X5R, CC0402_100NF_16V_10%_X7R, CC0402_100NF_16V_10%_X7R, CC0402_100NF_16V_10%_X5R, CC0402_100NF_16V_10%_X7R, CC0402_100NF_16V_10%_X7R, CC0402_100NF_16V_10%_X5R, CC0402_100NF_16V_10%_X5R, CC0402_100NF_16V_10%_X7R, CC0402_100NF_16V_10%_X7R, CC0402_100NF_16V_10%_X7R, CC0402_100NF_16V_10%_X7R, CC0402_100NF_16V_10%_X7R, CC0402_100NF_16V_10%_X7R, CC0402_100NF_16V_10%_X7R, CC0402_100NF_16V_10%_X7R, CC0402_100NF_16V_10%_X7R, CC0402_100NF_16V_10%_X7R, CC0402_100NF_16V_10%_X7R, CC0402_100NF_16V_10%_X7R, CC0402_100NF_16V_10%_X7R, CC0402_100NF_16V_10%_X7R, CC0402_100NF_16V_10%_X7R, CC0402_100NF_16V_10%_X7R, CC0402_100NF_16V_10%_X7R, CC0402_100NF_16V_10%_X7R, CC0402_100NF_16V_10%_X7R, CC0402_100NF_16V_10%_X7R, CC0402_100NF_16V_10%_X7R, CC0402_100NF_16V_10%_X7R, CC0402_100NF_16V_10%_X7R, CC0402_100NF_16V_10%_X7R, CC0402_100NF_16V_10%_X7R, CC0402_100NF_16V_10%_X7R, CC0402_100NF_16V_10%_X7R, CC0402_100NF_16V_10%_X7R, CC0402_100NF_16V_10%_X7R, CC0402_100NF_16V_10%_X7R, CC0402_100NF_16V_10%_X7R, CC0402_100NF_16V_10%_X7R, CC0402_100NF_16V_10%_X7R, CC0402_100NF_16V_10%_X7R, CC0402_100NF_16V_10%_X7R, CC0402_100NF_16V_10%_X7R, CC0402_100NF_16V_10%_X7R, CC0402_100NF_16V_10%_X7R, CC0402_100NF_16V_10%_X7R, CC0402_100NF_16V_10%_X7R, CC0402_100NF_16V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 | 85
10nF | Non-polarised capacitor | C6, C64 | CAPC1608X87N | GENERIC | CC0603_10NF_50V_10%_X7R | 0.87mm | PHYCOMP | 223858615636 | SMD Multilayer Chip Ceramic Capacitor | CC0603_10NF_50V_10%_X7R | 2
22uF | Non-polarised capacitor | C8, C129, C130, C131, C137, C138, C139, C140, C141, C142, C149, C151 | CAPC2012X135N | GENERIC | CC0805_22UF_16V_10%_X5R | 1.35mm | TDK | C2012X5R1C226KT | SMD Multilayer Chip Ceramic Capacitor | CC0805_22UF_16V_10%_X5R | 12
680pF | Non-polarised capacitor | C56_1, C56_2, C56_3, C56_4, C56_5, C56_6, C56_7, C56_8, C56_9, C56_10, C56_11, C56_12, C56_13, C56_14, C56_15, C56_16, C56_17, C56_18, C56_19, C56_20, C56_21, C56_22, C56_23, C56_24, C56_25, C56_26, C56_27, C56_28, C56_29, C56_30, C56_31, C56_32 | CAPC2012X135N | GENERIC | CC0805_680PF_50V_5%_NP0 | 1.35mm | PHYCOMP | 223886115681 | SMD Multilayer Chip Ceramic Capacitor | CC0805_680PF_50V_5%_NP0 | 32
220pF | Non-polarised capacitor | C61_1, C61_2, C61_3, C61_4, C61_5, C61_6, C61_7, C61_8, C61_9, C61_10, C61_11, C61_12, C61_13, C61_14, C61_15, C61_16, C61_17, C61_18, C61_19, C61_20, C61_21, C61_22, C61_23, C61_24, C61_25, C61_26, C61_27, C61_28, C61_29, C61_30, C61_31, C61_32 | CAPC1608X87N | GENERIC | CC0603_220PF_50V_5%_NP0 | 0.87mm | PHYCOMP | 223886715221 | SMD Multilayer Chip Ceramic Capacitor | CC0603_220PF_50V_5%_NP0 | 32
2.2nF | Non-polarised capacitor | C62_1, C62_2, C62_3, C62_4, C62_5, C62_6, C62_7, C62_8, C62_9, C62_10, C62_11, C62_12, C62_13, C62_14, C62_15, C62_16, C62_17, C62_18, C62_19, C62_20, C62_21, C62_22, C62_23, C62_24, C62_25, C62_26, C62_27, C62_28, C62_29, C62_30, C62_31, C62_32 | CAPC3216X140N | GENERIC | CC1206_2.2NF_50V_5%_NP0 | 1.25mm | PHYCOMP | 2238 863 15222 | SMD Multilayer Chip Ceramic Capacitor | CC1206_2.2NF_50V_5%_NP0 | 32
1uF | Non-polarised capacitor | C63, C82, C96, C133, C144 | CAPC1608X87N | GENERIC | CC0603_1UF_25V_10%_X7R | 0.9mm | MURATA | GRM188R71E105KA12D | SMD Multilayer Chip Ceramic Capacitor | CC0603_1UF_25V_10%_X7R | 5
82pF | Non-polarised capacitor | C68, C71, C76, C77, C95 | CAPC1608X87N | GENERIC | CC0603_82PF_50V_5%_NP0 | 0.87mm | PHYCOMP | 223886715829 | SMD Multilayer Chip Ceramic Capacitor | CC0603_82PF_50V_5%_NP0 | 5
2.2uF | Non-polarised capacitor | C80, C81 | CAPC1608X87N | GENERIC | CC0603_2.2UF_16V_10%_X5R | 0.9mm | YAGEO | CC0603KRX5R7BB225 | SMD Multilayer Chip Ceramic Capacitor | CC0603_2.2UF_16V_10%_X5R | 2
S1411-46R | Surface Mount Clip for PCB Screening Covers | CLIP27, CLIP28, CLIP29, CLIP30, CLIP31, CLIP32, CLIP33, CLIP34, CLIP35, CLIP36, CLIP37, CLIP38, CLIP39, CLIP40, CLIP41, CLIP42, CLIP43, CLIP44, CLIP45, CLIP46, CLIP47, CLIP48, CLIP49, CLIP50, CLIP51, CLIP52 | CLIP_HOLLAND-SHIELDING_LC | HARWIN | S1411-46R |  |  |  | Surface Mount Clip for PCB Screening Covers, 1500 Serie | S1411-46R | 26
BAV199 | Serial Diode | D5_1, D5_2, D5_3, D5_4, D5_5, D5_6, D5_7, D5_8, D5_9, D5_10, D5_11, D5_12, D5_13, D5_14, D5_15, D5_16, D5_17, D5_18, D5_19, D5_20, D5_21, D5_22, D5_23, D5_24, D5_25, D5_26, D5_27, D5_28, D5_29, D5_30, D5_31, D5_32 | SOT95P240X110-3N | NXP SEMICONDUCTORS | BAV199 |  |  |  | Low-Leakage Double Diode | BAV199 | 32
SMBJ12A | Zener Diode | D10, D11 | DIOM5336X265N | FAIRCHILD SEMICONDUCTOR | SMBJ12A |  |  |  | Uni-Directional Transient Voltage Suppressor Diode | SMBJ12A | 2
160mA-48V | Fuse | F1, F2 | FUSRC3216X100N | TYCO ELECTRONICS | nanoSMDC016F |  |  |  | PolySwitch® PTC Overcurrent Protection Device | FUSR1206_TYCO-NANOSMD016F | 2
Use only in PCB | Fiducial Target | FTG1 | FIDUCIAL_TOP_C100-200 |  |  |  |  |  | Round Fiducial Target, Top Layer, 1.0mm, Top Solder 2.0mm, Keepout =2.0mm | FIDUCIAL_TARGET_C100-200 | 1
Use only in PCB | Fiducial Target | FTG2, FTG4 | FIDUCIAL_TOP_S100-200 |  |  |  |  |  | Square Fiducial Target, Top Layer, 1.0mm, Top Solder 2.0mm, Keepout =2.0mm | FIDUCIAL_TARGET_S100-200 | 2
Use only in PCB | Fiducial Target | FTG3 | FIDUCIAL_TOP_S200-400 |  |  |  |  |  | Square Fiducial Target, Top Layer, 2.0mm, Top Solder 4.0mm, Keepout =4.0mm | FIDUCIAL_TARGET_S200-400 | 1
Heat Sink No Pad | Heat Sink Without Pad | HS1 | HSINK_ATS_ATS-X50190G-C1-R0 | ADVENCED THERMAL SOLUTION (ATS) | ATS-X50190G-C1-R0 |  |  |  | 35.0 x 35.0 x 7.5 mm BGA Heat Sink - High Performance maxiFLOW/maxiGRIP-STD | HSINK_ATS_ATS-X50190G-C1-R0 | 1
CC6-1212DF-E | CONV DC/DC 6W DUAL 12V +-12V PCB | IC1 | CC6-1212DF-E | TDK-Lambda Americas Inc. | CC6-1212DF-E |  |  |  | CONV DC/DC 6W DUAL 12V +-12V PCB | CC6-1212DF-E | 1
OPA197ID | 36-V, Precision, Rail-to-Rail Input/Output, Low Offset Voltage, Operational Amplifiers | IC2_1, IC2_2, IC2_3, IC2_4, IC2_5, IC2_6, IC2_7, IC2_8, IC2_9, IC2_10, IC2_11, IC2_12, IC2_13, IC2_14, IC2_15, IC2_16, IC2_17, IC2_18, IC2_19, IC2_20, IC2_21, IC2_22, IC2_23, IC2_24, IC2_25, IC2_26, IC2_27, IC2_28, IC2_29, IC2_30, IC2_31, IC2_32 | SOIC127P600X175-8N | TEXAS INSTRUMENTS | OPA197ID |  |  |  | 36-V, Precision, Rail-to-Rail Input/Output, Low Offset Voltage, Operational Amplifiers | OPA197ID | 32
MAX6250ACSA+ | 1ppm/°C, Low-Noise, Precision, +5.000V Voltage Reference | IC3 | SOIC127P600X175-8N | MAXIM | MAX6250ACSA+ |  |  |  | 1ppm/°C, Low-Noise, Precision, +5.000V Voltage Reference | MAX6250ACSA+ | 1
LT1964ES5-BYP#TRMPBF | 200mA, Low Noise, Low Dropout Negative Micropower Regulator | IC4 | SOT95P280X100-5N | LINEAR TECHNOLOGY | LT1964ES5-BYP#TRMPBF |  |  |  | -1.22V to -20V, 200mA, Low Noise, Low Dropout Negative Micropower Regulator | LT1964ES5-BYP#TRMPBF | 1
SN65MLVD040RGZT | 4-Channel Half-Duplex M-LVDS Line Transceiver | IC8, IC9 | QFN50P700X700X100-49N-S420 | TEXAS INSTRUMENTS | SN65MLVD040RGZT |  |  |  | 4-Channel Half-Duplex M-LVDS Line Transceiver | SN65MLVD040RGZT | 2
AD5372BCPZ | 32-Channel, 16-Bit, Serial Input, Voltage Output Digital-to-Analog Converter | IC18 | QFN50P900X900X100-65N-S725 | ANALOG DEVICES | AD5372BCPZ |  |  |  | 32-Channel, 16-Bit, Serial Input, Voltage Output Digital-to-Analog Converter | AD5372BCPZ | 1
STM811SW16F | Microprocessor Reset Circuit | IC19 | SOT143N | ST MICROELECTRONICS | STM811SW16F |  |  |  | 2.93V Reset Threshold Voltage Microprocessor Reset Circuit | STM811SW16F | 1
SN74LV595APWT | 8-Bit Shift Register With 3-State Output Register | IC23 | SOP65P640X120-16N | TEXAS INSTRUMENTS | SN74LV595APWT |  |  |  | 8-Bit Shift Register With 3-State Output Register | SN74LV595APWT | 1
LT1763CS8#PBF | 1.22V to 20V 500mA, Low Noise, LDO Adjustable Micropower Regulator | IC27 | SOIC127P600X175-8N | LINEAR TECHNOLOGY | LT1763CS8#PBF |  |  |  | 1.22V to 20V 500mA, Low Noise, LDO Adjustable Micropower Regulator | LT1763CS8#PBF | 1
24AA02E48T-I/OT | 1.7V-5.5V, 2K I2C Serial EEPROM With EUI-48 Node Identity | IC32 | SOT95P280X145-5N | MICROCHIP TECHNOLOGY | 24AA02E48T-I/OT |  |  |  | 1.7V-5.5V, 2K I2C Serial EEPROM With EUI-48 Node Identity | 24AA02E48T-I/OT | 1
TPS62175DQC | 4.75-28VDC to 1-6VDC, 500mA Step-Down Converter With Sleep Mode | IC35 | SON50P200X300X80-11N-R94X250 | TEXAS INSTRUMENTS | TPS62175DQC |  |  |  | 4.75-28VDC to 1-6VDC, 500mA Step-Down Converter With Sleep Mode | TPS62175DQC | 1
D-SUB | 68 contacts, AMPLIMITE .050", Right Angled Receptacle Series III | J1 | TYCO_5787082-7 | TYCO ELECTRONICS | 5787082-7 |  |  |  | 68 contacts, AMPLIMITE .050", Right Angled Receptacle Series III | TYCO_5787082-7 | 1
Header 16 | Connector 16 Male | J2 | 3M_N2516-6002RB | 3M | N2516-6002RB |  |  |  | 16 Contacts - Straight .100'' x .100'' Low Profile Four-Wall Header, 2500 Series | 3M_N2516-6002RB | 1
Header 26 | Connector 26 Male | J3, J4, J5, J7 | 3M_N2526-6002RB | 3M | N2526-6002RB |  |  |  | 26 Contacts - Straight .100'' x .100'' Low Profile Four-Wall Header, 2500 Series | 3M_N2526-6002RB | 4
Familly | Connector 30 Male | J37 | 3M_N2530-6002RB | 3M | N2530-6002RB |  |  |  | 30 Contacts - Straight .100'' x .100'' Low Profile Four-Wall Header, 2500 Series | 3M_N2530-6002RB | 1
10uH | Inductor With Core | L1, L6, L7, L8, L9, L15, L16 | IND_MURATA-PS_8400 | MURATA POWER SOLUTIONS | 84103C |  |  |  | Miniature Surface Mount Power Inductor (8400 Serie) | IND_10UH_10%_MURATA-PS_8400 | 7
2x6.5mH | Inductor Common Mode | L4_1, L4_2, L4_3, L4_4, L4_5, L4_6, L4_7, L4_8, L4_9, L4_10, L4_11, L4_12, L4_13, L4_14, L4_15, L4_16, L4_17, L4_18, L4_19, L4_20, L4_21, L4_22, L4_23, L4_24, L4_25, L4_26, L4_27, L4_28, L4_29, L4_30, L4_31, L4_32 | IND_WURTH_WE-SL2 | WURTH ELEKTRONIK | 744229 |  |  |  | Common Mode SMD Line Filter (WE-SL2 Serie) | IND_6.5MH_50%_WURTH_WE-SL2-744229 | 32
Green | LED x4 Green 1C2A-BOT_3C4A_5C6A_7C8A-TOP | LD4, LD5 | LED_BIVAR_H485CGDL | BIVAR | H485CGDL |  |  |  | Quad-Level 2mm Green LED, PCB Edge Mounting | LED_BIVAR_H485CGDL | 2
Undefined | Resistor | R1, R68_1, R68_2, R68_3, R68_4, R68_5, R68_6, R68_7, R68_8, R68_9, R68_10, R68_11, R68_12, R68_13, R68_14, R68_15, R68_16, R68_17, R68_18, R68_19, R68_20, R68_21, R68_22, R68_23, R68_24, R68_25, R68_26, R68_27, R68_28, R68_29, R68_30, R68_31, R68_32 | RESC1608X55N | Undefined | R0603_NO-VALUE | Undefined | Undefined | Undefined | Reserved Footprint For a 0603 (1608) Chip Resistor | R0603_NO-VALUE | 33
0 | Resistor | R2, R3, R11, R13, R14, R51, R88, R97, R99, R101 | RESC1005X40N | GENERIC | R0402_0R_JUMPER | 0.4mm | YAGEO PHYCOMP | 232270591001L | 1A (0.05R Max DC Resistance) Zero Ohm Jumper | R0402_0R_JUMPER | 10
36 | Resistor - 1% | R4 | RESC1608X55N | GENERIC | R0603_36R_1%_0.1W_100PPM | 0.55mm | NIC COMPONENT | NRC06F36R0TRF | General Purpose Thick Film Chip Resistor | R0603_36R_1%_0.1W_100PPM | 1
1k | Resistor - 1% | R5_1, R5_2, R5_3, R5_4, R5_5, R5_6, R5_7, R5_8, R5_9, R5_10, R5_11, R5_12, R5_13, R5_14, R5_15, R5_16, R5_17, R5_18, R5_19, R5_20, R5_21, R5_22, R5_23, R5_24, R5_25, R5_26, R5_27, R5_28, R5_29, R5_30, R5_31, R5_32, R7_1, R7_2, R7_3, R7_4, R7_5, R7_6, R7_7, R7_8, R7_9, R7_10, R7_11, R7_12, R7_13, R7_14, R7_15, R7_16, R7_17, R7_18, R7_19, R7_20, R7_21, R7_22, R7_23, R7_24, R7_25, R7_26, R7_27, R7_28, R7_29, R7_30, R7_31, R7_32 | RESC1608X55N | GENERIC | R0603_1K_1%_0.1W_100PPM | 0.55mm | NIC COMPONENT | NRC06F1001TRF | General Purpose Thick Film Chip Resistor | R0603_1K_1%_0.1W_100PPM | 64
100 | Resistor - 1% | R6, R16, R17, R18, R19, R20, R21, R22, R23, R141, R144, R147, R151, R157, R160, R163, R166, R170 | RESC1005X40N | GENERIC | R0402_100R_1%_0.1W_100PPM_50V | 0.4mm | PANASONIC | ERJ2RKF1000X | General Purpose Thick Film Chip Resistor | R0402_100R_1%_0.1W_100PPM | 18
220 | Resistor - 1% | R8, R9, R10, R12, R58, R82, R113, R114, R115, R116, R117, R118, R119, R120, R121, R122, R123 | RESC1608X55N | GENERIC | R0603_220R_1%_0.1W_100PPM | 0.55mm | NIC COMPONENT | NRC06F2200TRF | General Purpose Thick Film Chip Resistor | R0603_220R_1%_0.1W_100PPM | 17
2k32 | Resistor - 0.1% | R24_1, R24_2, R24_3, R24_4, R24_5, R24_6, R24_7, R24_8, R24_9, R24_10, R24_11, R24_12, R24_13, R24_14, R24_15, R24_16, R24_17, R24_18, R24_19, R24_20, R24_21, R24_22, R24_23, R24_24, R24_25, R24_26, R24_27, R24_28, R24_29, R24_30, R24_31, R24_32 | RESC1608X55N | GENERIC | R0603_2K32_0.1%_0.063W_10PPM | 0.5mm | TYCO HOLSWORTHY | RN73C1J2K32BTDF | Thin Film Chip Resistor | R0603_2K32_0.1%_0.063W_10PPM | 32
9k09 | Resistor - 0.1% | R25_1, R25_2, R25_3, R25_4, R25_5, R25_6, R25_7, R25_8, R25_9, R25_10, R25_11, R25_12, R25_13, R25_14, R25_15, R25_16, R25_17, R25_18, R25_19, R25_20, R25_21, R25_22, R25_23, R25_24, R25_25, R25_26, R25_27, R25_28, R25_29, R25_30, R25_31, R25_32 | RESC1608X55N | GENERIC | R0603_9K09_0.1%_0.063W_10PPM | 0.5mm | TYCO HOLSWORTHY | RN73C1J9K09BTDF | Thin Film Chip Resistor | R0603_9K09_0.1%_0.063W_10PPM | 32
11k | Resistor - 1% | R67_1, R67_2, R67_3, R67_4, R67_5, R67_6, R67_7, R67_8, R67_9, R67_10, R67_11, R67_12, R67_13, R67_14, R67_15, R67_16, R67_17, R67_18, R67_19, R67_20, R67_21, R67_22, R67_23, R67_24, R67_25, R67_26, R67_27, R67_28, R67_29, R67_30, R67_31, R67_32 | RESC1608X55N | GENERIC | R0603_11K_1%_0.1W_100PPM | 0.55mm | NIC COMPONENT | NRC06F1102TRF | General Purpose Thick Film Chip Resistor | R0603_11K_1%_0.1W_100PPM | 32
24k | Resistor - 1% | R69, R150 | RESC1608X55N | GENERIC | R0603_24K_1%_0.1W_100PPM | 0.55mm | NIC COMPONENT | NRC06F2402TRF | General Purpose Thick Film Chip Resistor | R0603_24K_1%_0.1W_100PPM | 2
2k7 | Resistor - 1% | R70, R153 | RESC1608X55N | GENERIC | R0603_2K7_1%_0.1W_100PPM | 0.55mm | YAGEO PHYCOMP | RC0603FR-072K7L | General Purpose Thick Film Chip Resistor | R0603_2K7_1%_0.1W_100PPM | 2
270k | Resistor - 1% | R162 | RESC1608X55N | GENERIC | R0603_270K_1%_0.1W_100PPM | 0.55mm | NIC COMPONENT | NRC06F2703TRF | General Purpose Thick Film Chip Resistor | R0603_270K_1%_0.1W_100PPM | 1
82k | Resistor - 1% | R164 | RESC1608X55N | GENERIC | R0603_82K_1%_0.1W_100PPM | 0.55mm | NIC COMPONENT | NRC06F8202TRF | General Purpose Thick Film Chip Resistor | R0603_82K_1%_0.1W_100PPM | 1
10k | Resistor - 1% | R171 | RESC1005X40N | GENERIC | R0402_10K_1%_0.0625W_100PPM | 0.4mm | YAGEO PHYCOMP | 232270671003L | General Purpose Thick Film Chip Resistor | R0402_10K_1%_0.0625W_100PPM | 1
10k | Thermistor NTC (Negative Temperature Coefficient) | RT1 | THERMC1608X90N | EPCOS | B57330V2103J260 |  |  |  | SMD NTC Thermistor for Temperature Measurement | THERM_NTC_10K_EPCOS_B57330V2103J260 | 1
CP20147H | Peltier Module 15x15 mm | TEC1 | TEC_CP20147H |  |  |  |  |  |  |  | 1
Test Point | Test Point | TP1, TP2, TP3, TP4, TP5, TP6, TP7, TP8, TP9, TP10, TP11, TP12, TP13, TP14, TP15, TP16, TP17 | TPS127 |  |  |  |  |  | 1.27mm x 1.27mm PCB Copper Area (SMD Test Point) | SMD_PAD_1.27X1.27MM | 17

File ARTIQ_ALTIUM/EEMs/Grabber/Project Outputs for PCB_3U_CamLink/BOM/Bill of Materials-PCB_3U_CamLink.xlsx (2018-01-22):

Comment | Description | Designator | Footprint | Manufacturer | Manufacturer Part Number | Manufacturer1 ComponentHeight | Manufacturer1 Example | Manufacturer1 Part Number | Part Description | Part Number | Quantity
Plated Hole | Single Terminal Socket | B1, B2, B3, B4, B5, B6, B7, B8, B9, B10, B11 | c130h60 |  |  |  |  |  | Plated Through Hole: Hole Dia.=0.6mm Pad Dia.=1.3mm | PLATED_HOLE0.6_PAD1.3 | 11
100nF | Non-polarised capacitor | C47A, C47B, C47C, C47D, C47E, C47F, C47G, C47H, C47I, C47J, C47K, C47L, C47M, C47N, C47O, C47P, C58, C59, C64, C65, C67 | CAPC1005X55N | GENERIC | CC0402_100NF_16V_10%_X5R | 0.55mm | MURATA | GRM155R61C104KA88D | SMD Multilayer Chip Ceramic Capacitor | CC0402_100NF_16V_10%_X5R | 21
10uF | Polarised capacitor | C62 | CAPAE430X540N | PANASONIC | EEEFK1C100AR |  |  |  | Aluminum Electrolytic SMT Capacitor | CAE430-540_10UF_16V_20% | 1
22uF | Non-polarised capacitor | C66, C68 | CAPC2012X135N | GENERIC | CC0805_22UF_16V_10%_X5R | 1.35mm | TDK | C2012X5R1C226KT | SMD Multilayer Chip Ceramic Capacitor | CC0805_22UF_16V_10%_X5R | 2
NUP4114UPXV6T1G |  | D1A, D1B, D1C, D1D, D1E, D1F, D1G, D1H, D1I, D1J, D1K, D1L, D1M, D1N, D1O, D1P | SOTFL50P160X60-6N | ON SEMICONDUCTOR | NUP4114UPXV6T1G |  |  |  | ESD Protection Diodes Array (8kV) with Low Clamping Voltage | NUP4114UPXV6T1G | 16
Use only in PCB | Fiducial Target | FTG21 | FIDUCIAL_TOP_C100-200 |  |  |  |  |  | Round Fiducial Target, Top Layer, 1.0mm, Top Solder 2.0mm, Keepout =2.0mm | FIDUCIAL_TARGET_C100-200 | 1
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

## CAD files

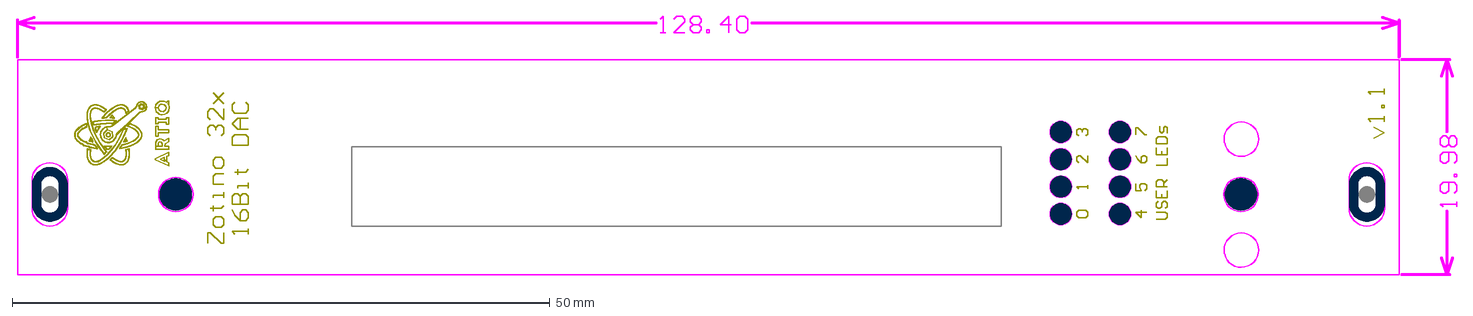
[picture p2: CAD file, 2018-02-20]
ARTIQ_ALTIUM/PANELS/Project Outputs for PANELS/AutoCAD PCB/PANEL_3U_DAC.DXF
133.9 x 24.2 mm

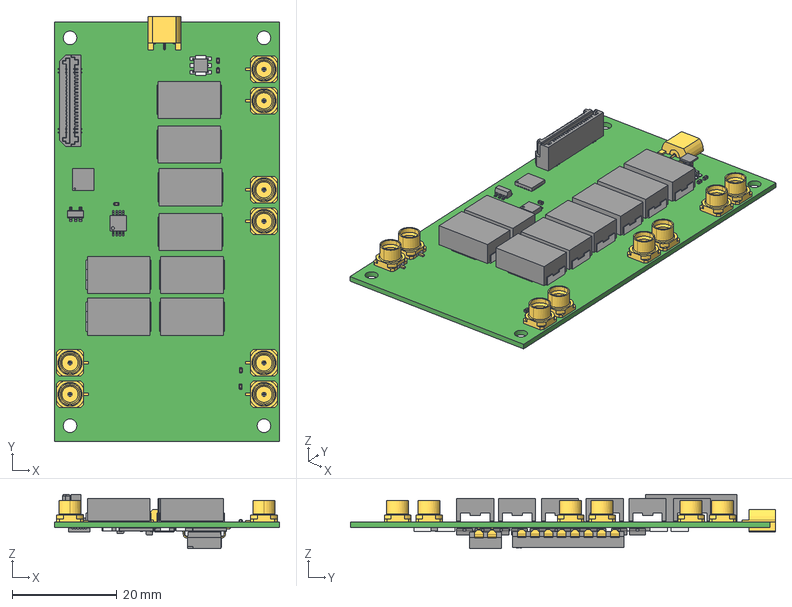
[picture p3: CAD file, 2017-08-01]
ARTIQ_ALTIUM/PCB_eRTM15_Baikal/PCB_mezzanine_clock_template.step
43.0 x 81.1 x 10.3 mm
Board
SOT95P285X140-3N x 8
SOT95P240X110-3N x 4
SW_OMRON_A6S-8102-H
SW_OMRON_A6S-2102-H
RESC1005X40N x 12
RESC6331X70N x 8
RESC3216X65N x 10
QFN50P400X400X80-25N-S255 x 2
CAPC1005X55N x 5
SOP65P490X109-8N
SOT95P280X145-5N
MOLEX_85305-0232 x 8
SAMTEC_LSS-120-03-L-DV-A
XFMR_MINI-CIRCUITS_DB1627

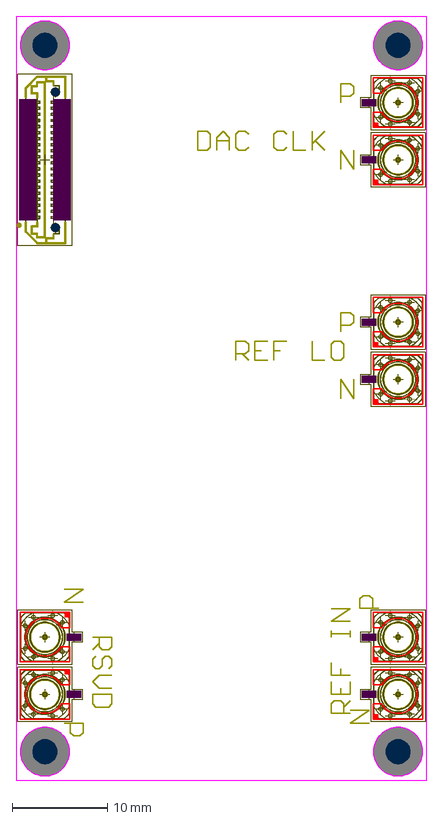
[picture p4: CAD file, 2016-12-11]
ARTIQ_ALTIUM/PCB_mezzanine_clock/Clock_Mezzanine.DXF
43.1 x 80.0 mm

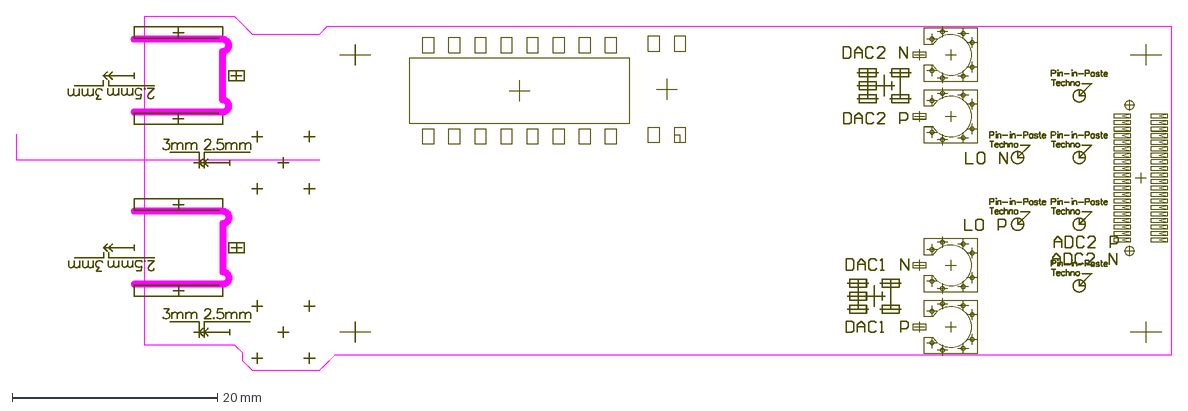
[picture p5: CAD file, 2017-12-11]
ARTIQ_ALTIUM/Sayma_AFEs/TestMod/AFE_mezzanine.DXF
112.5 x 34.5 mm

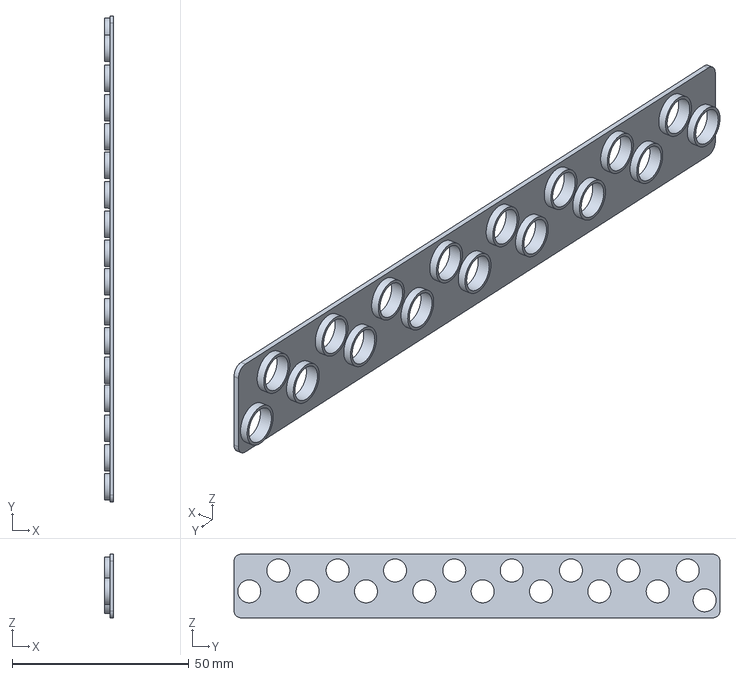
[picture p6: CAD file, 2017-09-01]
MECH/PANELS/isolation panel.stp
2.50 x 137.4 x 18.0 mm

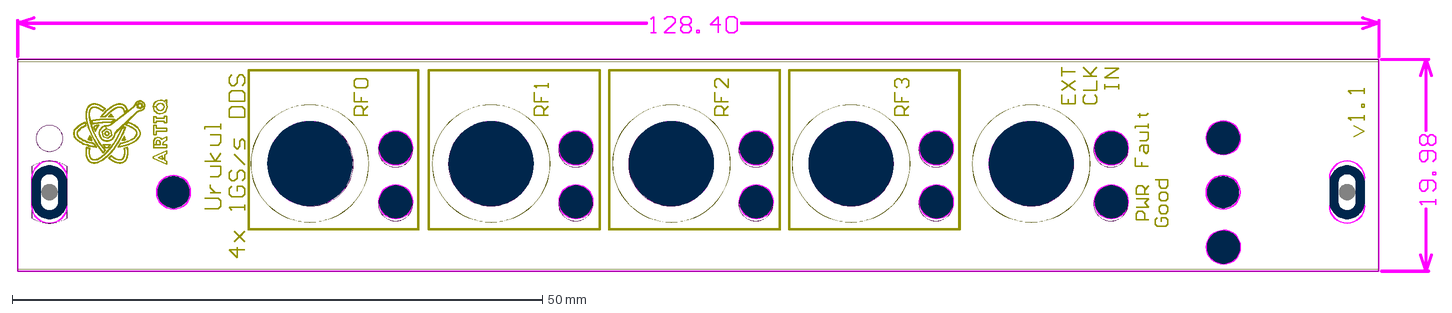
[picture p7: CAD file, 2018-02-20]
ARTIQ_ALTIUM/PANELS/Project Outputs for PANELS/AutoCAD PCB/Panel_Urukul.DXF
133.9 x 24.2 mm

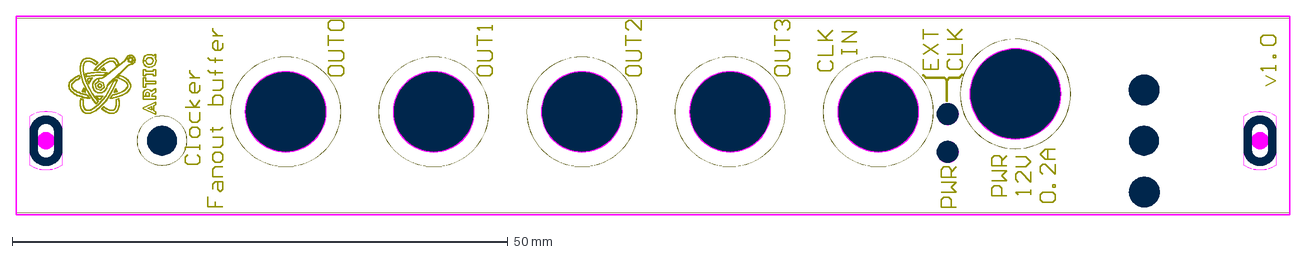
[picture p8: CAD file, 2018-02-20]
ARTIQ_ALTIUM/PANELS/Project Outputs for PANELS/AutoCAD PCB/Panel_3U_CLK_DIS.DXF
128.4 x 20.0 mm

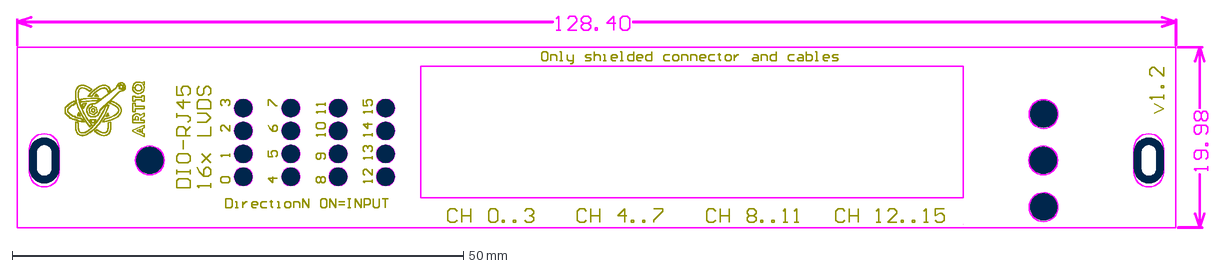
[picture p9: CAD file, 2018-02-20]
ARTIQ_ALTIUM/PANELS/Project Outputs for PANELS/AutoCAD PCB/PANEL_3U_RJ45.DXF
132.1 x 23.6 mm

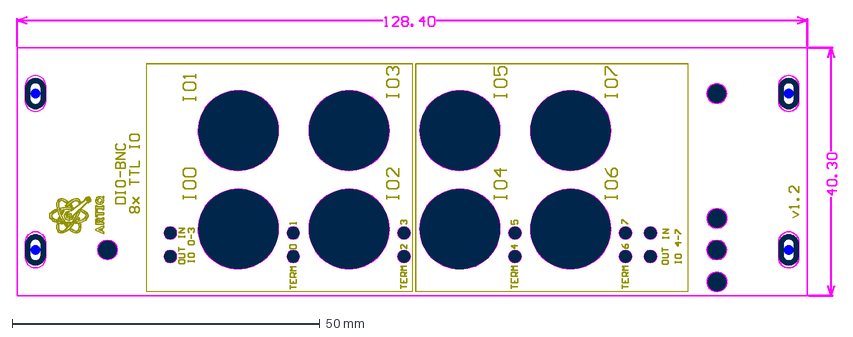
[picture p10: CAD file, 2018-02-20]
ARTIQ_ALTIUM/PANELS/Project Outputs for PANELS/AutoCAD PCB/PANEL_3U_BNC.DXF
133.3 x 45.5 mm

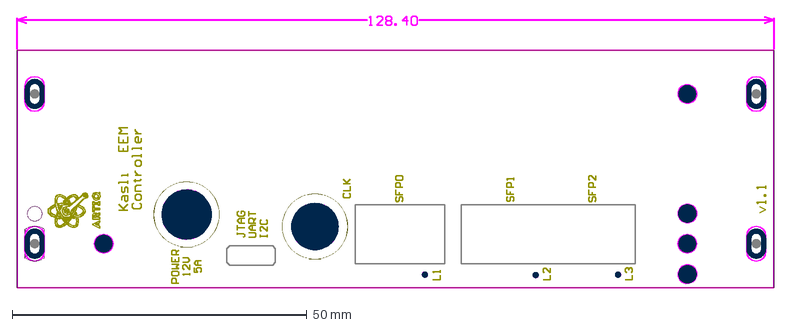
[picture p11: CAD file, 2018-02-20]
ARTIQ_ALTIUM/PANELS/Project Outputs for PANELS/AutoCAD PCB/PANEL_3U_KASLI.DXF
128.7 x 46.0 mm

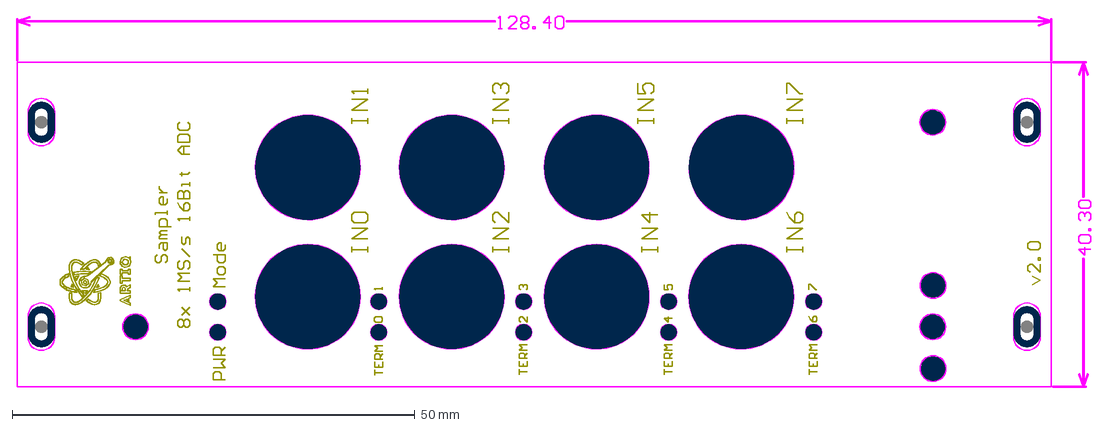
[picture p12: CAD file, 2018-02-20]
ARTIQ_ALTIUM/PANELS/Project Outputs for PANELS/AutoCAD PCB/Sampler.DXF
133.4 x 46.1 mm

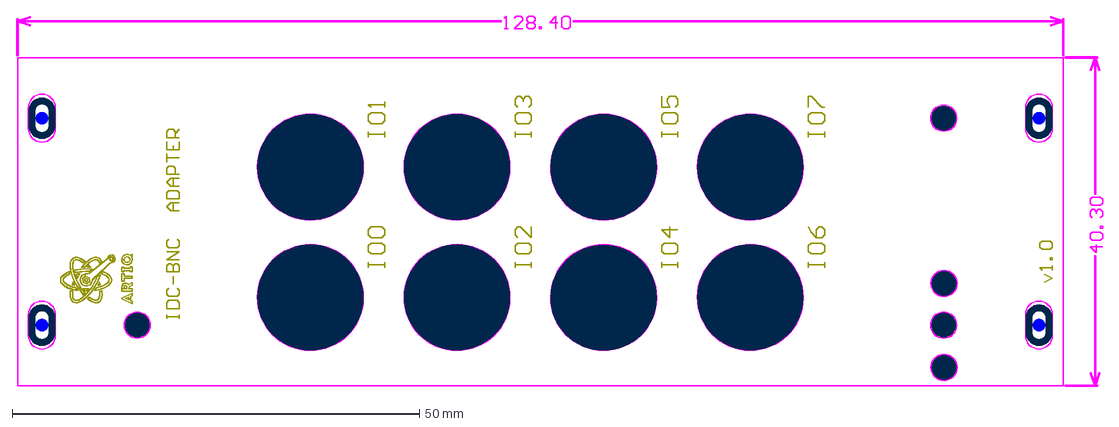
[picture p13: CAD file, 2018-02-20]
ARTIQ_ALTIUM/PANELS/Project Outputs for PANELS/AutoCAD PCB/PANEL_DAC_BNC_Adapter.DXF
133.3 x 45.5 mm

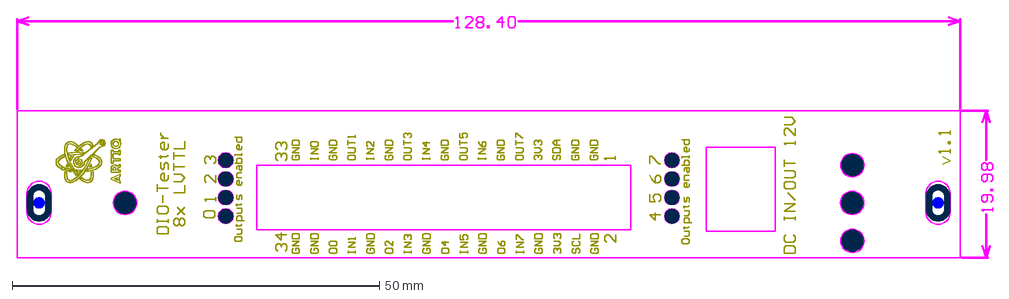
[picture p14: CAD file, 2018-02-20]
ARTIQ_ALTIUM/PANELS/Project Outputs for PANELS/AutoCAD PCB/PANEL_3U_Tester.DXF
133.0 x 33.0 mm

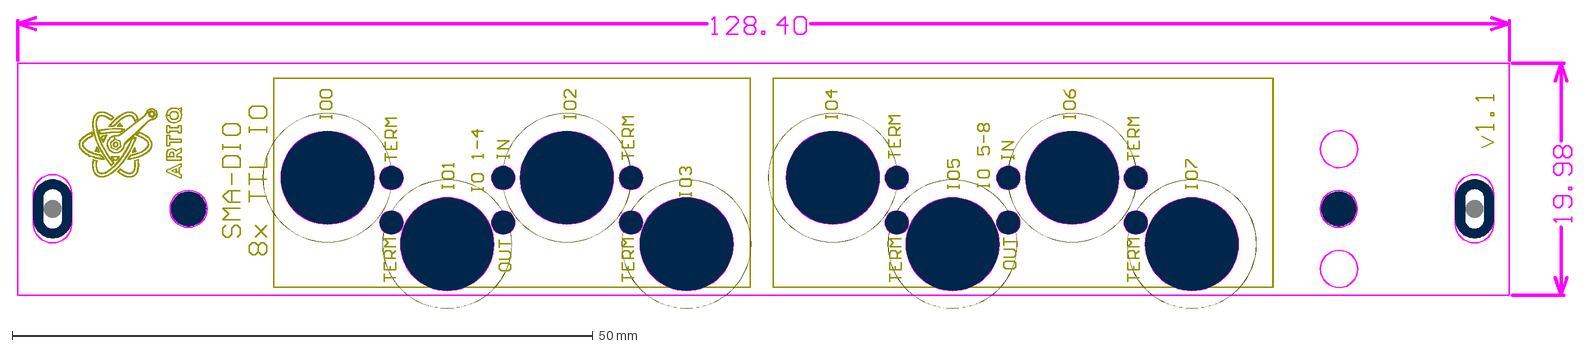
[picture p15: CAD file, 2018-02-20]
ARTIQ_ALTIUM/PANELS/Project Outputs for PANELS/AutoCAD PCB/PANEL_3U_SMA.DXF
133.9 x 25.2 mm

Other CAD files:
ARTIQ_ALTIUM/PANELS/Project Outputs for PANELS/AutoCAD PCB/PANEL_HD68-IDC_Adapter.DWG
ARTIQ_ALTIUM/PANELS/Project Outputs for PANELS/AutoCAD PCB/Panel_Grabber.DWG
ARTIQ_ALTIUM/PANELS/Project Outputs for PANELS/AutoCAD PCB/PANEL_3U_VHDCI_Breakout.DXF
ARTIQ_ALTIUM/Sayma_AFEs/TestMod/AFE_mezzanine.DWG

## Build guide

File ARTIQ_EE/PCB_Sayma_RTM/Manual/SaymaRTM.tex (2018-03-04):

\documentclass[12pt,a4paper,final,titlepage]{article}
\addtolength{\textwidth}{3cm}
\addtolength{\hoffset}{-1.5cm}
\addtolength{\textheight}{3cm}
\addtolength{\voffset}{-1.5cm}
\usepackage[utf8]{inputenc}
\usepackage[english]{babel}
\usepackage[T1]{fontenc}
\usepackage{textcomp}
\usepackage{gensymb}
\usepackage{amsmath}
\usepackage[textwidth=40]{todonotes}
%\usepackage{todonotes}
%\usepackage[disable]{todonotes}
\usepackage{titlesec}
\usepackage{amsfonts}
\usepackage{amssymb}
\usepackage{gensymb}
\usepackage{longtable}
\usepackage{makeidx}
\usepackage{indentfirst}
\usepackage{graphicx}
%\usepackage{tabularx}
\usepackage{epstopdf}
\usepackage{lmodern}
\usepackage{color}
\usepackage{xcolor}
\usepackage{url}
\usepackage{subfiles}
\usepackage{hhline}
\usepackage{nameref}
\usepackage{float}
\usepackage{wrapfig}
\usepackage{lastpage}
\makeatletter
\newcommand*{\currentname}{\@currentlabelname}
\makeatother
\usepackage{caption}
\usepackage[printwatermark]{xwatermark}
\usepackage{pdfpages}
\usepackage{multirow}
\usepackage{svg}
\setsvg{inkscape = inkscape -z -D}
\usepackage[toc,page]{appendix}
\usepackage{caption}
\usepackage{listings}
\graphicspath{{./},{./img/}}
\newcommand{\figref}{Fig.~\ref}
%\renewcommand{\bibname}{References}
\definecolor{gray}{rgb}{0.4,0.4,0.4}
\definecolor{lgray}{rgb}{0.8,0.8,0.8}
\definecolor{lred}{rgb}{1,0.4,0.4}
\definecolor{darkblue}{rgb}{0.0,0.0,0.6}
\definecolor{cyan}{rgb}{0.0,0.6,0.6}
\newwatermark*[allpages,color=lred,angle=-45,scale=1,xpos=105,ypos=118]{DRAFT}
\newwatermark*[allpages,scale=0.4,xpos=-57,ypos=120]{}
\newwatermark*[allpages,scale=0.3,xpos=-35,ypos=122]{}
%\usepackage[left=2cm,right=2cm,top=2cm,bottom=2cm]{geometry}
\usepackage{fancyhdr}
\pagestyle{fancy}
\lhead{}
\rhead{\nazwa}
\rfoot{Page \thepage \hspace{1pt} of \pageref{LastPage}}
\usepackage{hyperref}
\hypersetup{
	colorlinks,
	citecolor=black,
	filecolor=black,
	linkcolor=black,
	urlcolor=black
}
\sloppy

%\renewcommand{\bibname}{References}
%-----------------------------------------------------------------------
\newcommand{\nazwa}{SAYMA RTM}

%-----------------------------------------------------------------------
%zaczynaj każdą sekcję na nowej stronie

\pdfinfo{ /Author (ISE) /Title (\nazwa) /Keywords (XXXX) }

\renewcommand{\footrulewidth}{1pt}

\cfoot{}

\begin{document}

\input{tex/title.tex}
%\maketitle
\input{tex/hist.tex}
\clearpage

\listoftodos
\clearpage
\tableofcontents

%\todo[inline]{\currentname: do FMC podpiety jest tylko 1 MGT, ale to jeszcze poprawie. }
%\todo[inline]{\currentname: ...}

\clearpage

\input{tex/glossary.tex}
\clearpage

\input{tex/wiki_utca.tex}
\clearpage

\input{tex/description.tex}
\clearpage

\input{tex/view.tex}
\clearpage

\input{tex/routing.tex}
\clearpage

\input{tex/panel.tex}
\clearpage

\input{tex/AFEmezzanine.tex}
\clearpage

\input{tex/clock.tex}
\clearpage

\input{tex/CLKdist.tex}
\clearpage

\input{tex/housekeeping.tex}
\clearpage

\input{tex/power.tex}
\clearpage

\input{tex/testing.tex}
\clearpage

\begin{appendix}

\input{tex/appendix.tex}
\clearpage

\input{tex/technical.tex}
\clearpage

\end{appendix}

\end{document}

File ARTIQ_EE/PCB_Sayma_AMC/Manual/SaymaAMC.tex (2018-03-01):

\documentclass[12pt,a4paper,final,titlepage]{article}
\addtolength{\textwidth}{3cm}
\addtolength{\hoffset}{-1.5cm}
\addtolength{\textheight}{3cm}
\addtolength{\voffset}{-1.5cm}
\usepackage[utf8]{inputenc}
\usepackage[english]{babel}
\usepackage[T1]{fontenc}
\usepackage{textcomp}
\usepackage{gensymb}
\usepackage{amsmath}
\usepackage[textwidth=40]{todonotes}
%\usepackage{todonotes}
%\usepackage[disable]{todonotes}
\usepackage{titlesec}
\usepackage{amsfonts}
\usepackage{amssymb}
\usepackage{gensymb}
\usepackage{longtable}
\usepackage{makeidx}
\usepackage{indentfirst}
\usepackage{graphicx}
\usepackage{amsmath}
\usepackage{epstopdf}
\usepackage{lmodern}
\usepackage{color}
\usepackage{xcolor}
\usepackage{url}
\usepackage{subfiles}
\usepackage{hhline}
\usepackage{nameref}
\usepackage{float}
\usepackage{wrapfig}
\usepackage{lastpage}
\makeatletter
\newcommand*{\currentname}{\@currentlabelname}
\makeatother
\usepackage{caption}
\usepackage[printwatermark]{xwatermark}
\usepackage{pdfpages}
\usepackage{multirow}
\usepackage{svg}
\setsvg{inkscape = inkscape -z -D}
\usepackage[toc,page]{appendix}
\usepackage{caption}
\usepackage{listings}

\usepackage[printonlyused,withpage]{acronym}
\graphicspath{{./},{./img/}}
\newcommand{\figref}{Fig.~\ref}
%\renewcommand{\bibname}{References}
\definecolor{gray}{rgb}{0.4,0.4,0.4}
\definecolor{lgray}{rgb}{0.8,0.8,0.8}
\definecolor{lred}{rgb}{1,0.4,0.4}
\definecolor{darkblue}{rgb}{0.0,0.0,0.6}
\definecolor{cyan}{rgb}{0.0,0.6,0.6}
\newwatermark*[allpages,color=lred,angle=-45,scale=1,xpos=105,ypos=118]{DRAFT}
\newwatermark*[allpages,scale=0.4,xpos=-57,ypos=120]{}
\newwatermark*[allpages,scale=0.3,xpos=-35,ypos=122]{}
%\usepackage[left=2cm,right=2cm,top=2cm,bottom=2cm]{geometry}
\usepackage{fancyhdr}
\pagestyle{fancy}
\lhead{}
\rhead{\nazwa}
\rfoot{Page \thepage \hspace{1pt} of \pageref{LastPage}}
\usepackage{hyperref}
\hypersetup{
	colorlinks,
	citecolor=black,
	filecolor=black,
	linkcolor=black,
	urlcolor=black
}
\sloppy

%-----------------------------------------------------------------------
\newcommand{\nazwa}{SAYMA AMC}

\pdfinfo{ /Author (ISE) /Title (\nazwa) /Keywords (XXXX) }

\renewcommand{\footrulewidth}{1pt}

\cfoot{}

\begin{document}

\input{tex/title.tex}
%\maketitle
\input{tex/hist.tex}
\clearpage

\listoftodos
\clearpage
\tableofcontents

\clearpage

\input{tex/wiki_introduction.tex}
\clearpage

\input{tex/wiki_utca.tex}
\clearpage

\input{tex/wiki_sayma.tex}
\clearpage

%\input{tex/intro.tex}
%\clearpage

%\input{tex/description.tex}
%\clearpage

\input{tex/view.tex}
\clearpage

\input{tex/routing.tex}
\clearpage

\input{tex/clocking.tex}
\clearpage

\input{tex/panel.tex}
\clearpage

\input{tex/fmc.tex}
\clearpage

\input{tex/usb-uart.tex}
\clearpage

\input{tex/jtag.tex}
\clearpage

%\input{tex/fpga.tex}
%\clearpage

\input{tex/power.tex}
\clearpage

\input{tex/mmc.tex}
\clearpage

\input{tex/housekeeping.tex}
\clearpage

\input{tex/signals.tex}
\clearpage

\input{tex/testing.tex}
\clearpage

\begin{appendix}

\input{tex/appendix.tex}
\clearpage

\input{tex/gateware.tex}
\clearpage

\end{appendix}

\end{document}

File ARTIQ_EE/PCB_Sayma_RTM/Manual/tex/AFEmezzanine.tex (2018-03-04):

\section{RF Front-End Mezzanines}\label{rf-front-end-mezzanines}

Mezzanines providing analogue front-ends (AFEs) for the ADCs and DACs on
Sayma.

\section{Available AFEs}\label{available-afes}

\subsection{TestMod}\label{testmod}

Simple mezzanine designed for thermal and connectivity testing, and to
serve as a template for other mezzanine designs.

\todo[inline]{image}

Design files are
\href{https://github.com/m-labs/sinara/tree/master/ARTIQ_ALTIUM/Sayma_AFEs/TestMod}{here},
the schematic is
\href{https://github.com/m-labs/sinara/tree/master/ARTIQ_ALTIUM/Sayma_AFEs/TestMod/AFE_mezzanine.PDF}{here}.

\subsection{BaseMod}\label{basemod}

BaseMod is a base-band input/output mezzanine. Design files are
\href{https://github.com/m-labs/sinara/tree/master/ARTIQ_ALTIUM/Sayma_AFEs/BaseMod}{here}.
\todo[inline]{there are no sch in pdf}
%the schematic is
%\href{https://github.com/m-labs/sinara/blob/master/ARTIQ_ALTIUM/PCB_mezzanine_analog_allaki/Project\%20Outputs\%20for\%20allaki_mezzanine/allaki_mezzanine.PDF}{here}.

NB: 12/2017 Allaki was
\href{https://github.com/m-labs/sinara/issues/396}{renamed} BaseMod.

\todo[inline]{image}

\subsubsection{Outputs}\label{outputs}

BaseMod provides two independent RF outputs, featuring:

\begin{itemize}

	\item
	\textbf{Bandwidth}: 10MHz - 4GHz (upper frequency is limited by
	several different components)
	\item
%	\textbf{Max output power}: ?dBm (limited by ?).
	\item
	\textbf{Output filters}: either 3 Mini-Circuits FV1206 series filters,
	or a user-definable discrete 9-pole discrete-element filter using 0402
	components.
	\item
	\textbf{Low phase noise amplifier}: Mini-Circuits ERA-4XSM+); 14.2dBm
	gain at 1GHz.
	\item
	\textbf{Digitally programmable attenuator}: HMC542BLP4E; 0dB to 31.dB
	in 0.5dB steps; controllable in real-time.
	\item
	\textbf{Fast, high-isolation RF switch}: HMC349LP4C; 67dB isolation at
	1GHz; controllable in with real-time control.
	\item
	\textbf{Power detector}: AD8363ACPZ on switch ``off'' port for
	monitoring and power levelling.
	\item
	\textbf{Optional isolation of output grounds}: to avoid ground loops,
	achieved by fitting capacitors and washers.
\end{itemize}

\subsubsection{Inputs}\label{inputs}

BaseMod provides two independent inputs, each of which can be configured
(component placement) as:

\begin{enumerate}
	\def\labelenumi{\arabic{enumi}.}
	\item
	Direct feed to ADC via ADA4927-1 buffer for maximum bandwidth
	\item
	Low-noise programmable gain instrumentation amplifier (AD8253)
	front-end
\end{enumerate}

\begin{itemize}
	\item
	\textbf{Bandwidth}: DC-300kHz
	\item
	\textbf{Input ranges}: ±0.1V, ±1V, ±10V
	\item
	\textbf{Fully differential inputs}: 100k between each input signal and
	ground and the circuit ground
	\item
	\textbf{Filters}: Common-mode and differential mode filtering of RF
	interference for optimum DC precision
	\item
	\textbf{Input protection}: diodes between each input and the supply
	rails for maximum ruggedness
	\item
	Supports both high-speed input directly coupled into a high-speed
	pre-amp, and low-frequency inputs using a variable-gain
	instrumentation amplifier (choice by component selection). Pull
	details from \href{https://github.com/m-labs/sinara/issues/81}{\#81}
	\item
	Instrumentation amp: gain, filters, etc.
\end{itemize}

\subsection{MixMod}\label{mixmod}

MixMod is an up-converting mezzanine, using an analogue IQ mixer to mix
the input and output RF signals with a LO supplied by Sayma.

The LO provided by Sayma should be a 3V3 PECL square-wave.

Design files are
\href{https://github.com/m-labs/sinara/tree/master/ARTIQ_ALTIUM/Sayma_AFEs/MixMod}{here}
\href{https://github.com/m-labs/sinara/tree/master/ARTIQ_ALTIUM/Sayma_AFEs/BaseMod}{here}.
\todo[inline]{there are no sch in pdf}
\todo[inline]{image}

\subsubsection{Outputs}\label{outputs-1}

MixMod provides a single RF output between 2.5GHz and 3.5GHz, produced
by mixing two DAC channels with a LO supplied by Sayma. Other than the
IQ mixer, the output signal-chain is identical to BaseMod.

\subsubsection{Inputs}\label{inputs-1}

MixMod's two inputs can either be operated in baseband or downconversion
mode (selectable by component choice). In baseband mode, the inputs
function identically to BaseMod's. In downconversion mode, a single SMA
input feeds the RF port on an IQ mixer to produce a pair of baseband
signals, which then feed the two signal chains.

\section{Mezzanines Mechanical Specification}\label{general-specification}

\begin{itemize}

	\item Board size
		\begin{figure}[htbp!]
			\centering
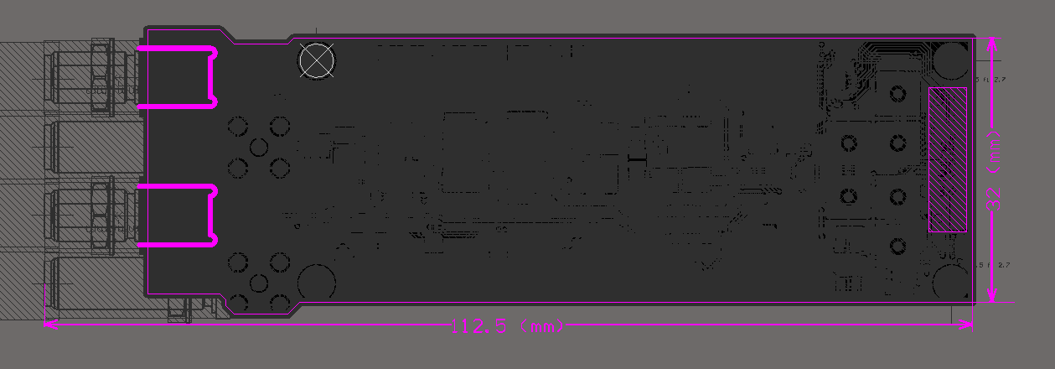
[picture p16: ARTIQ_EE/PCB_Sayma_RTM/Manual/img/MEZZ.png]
			\\
			\caption{Mezzaninne dimensions}
		\end{figure}	
	\item Mounting holes\\
	There are four mounting holes fi 2.7mm for M2.5 screws.
%	\item
%	SMA locations and pns
%	\item
%	Connectors
\end{itemize}

%\subsection{Electrical}\label{electrical}
%
%\begin{itemize}
%
%	\item
%	Suggest
%	\href{http://www.analog.com/en/products/rf-microwave/iq-modulators-demodulators/iq-modulators/adl5375.html}{ADL5375}
%	IQ modulator. Good intrinsic carrier/sideband rejection, relatively
%	low temp coefficients, sufficient IF bandwidth, good I/Q linearity.
%	This is the chip used in the NIST Magtrap drive system.
%\end{itemize}

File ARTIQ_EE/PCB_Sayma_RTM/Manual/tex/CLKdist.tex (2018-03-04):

\section{Clock distribution}

\subsection{Crate clock distribution}\label{crate-clock-distribution}

The crate distributes a 100MHz clock on a RTM RF backplane. This clock
is typically externally supplied from a high quality source, but it is
desirable to include a 100 MHz oscillator on the MCH RTM and on the
Sayma RTM the for turnkey/standalone operation (with limited timing
performance).

In a multi-crate system, all crates need to receive the same 100MHz
clock to support sample-accurate operation.

\subsection{RTIO}\label{rtio}

Sayma and Metlino shall include a general purpose XO of e.g.~125MHz,
connected to a general purpose FPGA clock input pin. This is a simple
addition that make the boards a bit friendlier to developers. It also
allows for debugging and bootstrapping of the clocks during development:
This XO becomes necessary if we use a transceiver PLL chip that needs to
be configured before it outputs a clock.

\subsubsection{Metlino}\label{metlino}

In root mode, the Metlino receives the 100MHz clock and turns it into a
200MHz RTIO clock that it uses as reference clock for its DRTIO
transmitters.

In satellite mode, the Metlino recovers the RTIO clock from the fiber.

The following clock resources should be available on Metlino to support
this operation:

\begin{itemize}

	\item
	Si5324 for 100-\textgreater{}200MHz in root mode, and CDR jitter
	filtering in satellite mode.
	\item
	Si5324 free-running based on local XO for providing a CDR reference in
	satellite mode.
\end{itemize}

The Si5324 shall have its two clock outputs connected to a transceiver
clock input (so that we can transmit back synchronously and at fixed
latency) and to a general purpose clock input on the FPGA.
Transceiver-fabric clock routing inside the FPGA is of poor quality, so
we want to mitigate that.

The Metlino will be double-width and connected to its RTM to receive the
100MHz RTM clock (required in root mode).

\subsubsection{Sayma}\label{sayma}

Sayma cards recover their RTIO clock from the backplane's transceiver
link or - if they are stand-alone -- from their SFP/SATA DRTIO
transciever link. This requires the same hardware as the Metlino in root
mode: Si5324 connected in the same way.

\subsection{DRTIO}\label{drtio}

DRTIO (distributed real-time input/output) achieves three distinct
things over a single high speed serial link:

\begin{itemize}

	\item
	It transfers the RTIO clock
	\item
	It transfers the RTIO time. This means that it will designate a
	specific RTIO clock cycle as timestamp zero.
	\item
	It transfers data. Data consists of RTIO events (outputs or inputs)
	and low bandwidth non-realtime auxiliary traffic.
\end{itemize}

%Note that the RTIO time (clock plus the cycle counter) is the primary
%and authoritative source of time in the ARTIQ tree. The RTIO clock is
%however not an extremely low noise clock that could serve as the sample
%clock in data conversion or as a base clock for picosecond level
%timestamping. Having another ``better'' clock do these tasks is not
%trivial since the alignment between such a sample clock and the RTIO
%clock is unknown. When data is transferred between the two clock domains
%it is undefined which RTIO cycle corresponds to which sample clock
%cycle.

\subsection{JESD204 synchronization
	procedure}\label{jesd204-synchronization-procedure}

While JESD204B subclass 1 provides ``fixed latency'' for the data
transfer between a converter (ADC or DAC) and the FPGA, this is
fundamentally insufficient for DRTIO. We need more than just fixed
latency. A JESD204B link has two deviceclocks: one for the converter and
one for the FPGA. The SYSREF signal is used to designate which cycle of
the faster of the two deviceclocks corresponds to the beginning of a
cycle in the slower deviceclock. The slower deviceclock and SYSREF have
an a priori unknown phase with respect to the RTIO clock.

Timestamping a certain sample to a specific RTIO cycle requires two
things in addition to JESD204B subclass 1 deterministic latency:

\begin{itemize}

	\item
	Reproducible alignment of the sample clock with the RTIO clock. This
	is guaranteed by fixed latencies in the DRTIO branch of the clocking
	(master oscillator -\textgreater{} MCH RTM -\textgreater{} Metlino
	-\textgreater{} AMC backplane DRTIO link -\textgreater{} Sayma AMC)
	and in the sample branch (master oscillator -\textgreater{} MCH RTM
	-\textgreater{} RF backplane -\textgreater{} Sayma RTM -\textgreater{}
	PLL -\textgreater{} clock distribution -\textgreater{} DAC/ADC). This
	also requires the backplane clock and the sample clock to be integer
	multiples of the RTIO clock.
	\item
	Reproducible alignment of SYSREF and the slower FPGA deviceclock to
	the RTIO clock. This is done actively.
\end{itemize}

The FPGA shall align SYSREF with designated RTIO clock edges. The
alignment should be better than a DAC clock cycle and reproducible
across reboots.

The FPGA first roughly aligns SYSREF within one cycle before a desired
RTIO clock edge by asserting the synchronization signal of the clock
chip, which resets its dividers. This alignment is optional and may have
an uncertainty of several DAC clock cycles. It is only used to decrease
the required scan range of the delay elements used in the next steps.

The FPGA then analyzes SYSREF by repeatedly sampling it with the RTIO
clock while scanning a calibrated I/O input delay. This measures the
SYSREF phase with a high precision.

The delay scan mechanism is limited by the resolution and stability of
the scan element. The resolution must be significantly smaller than a
DAC clock period. There are three delay elements available to perform
the scan:

\begin{itemize}

	\item
	IDELAYE3 in the FPGA. Uncertainty about PVT effects.
	\item
	Digital delay in the clock distribution chip. Infinite delay, low
	noise.
	\item
	Analog delay in the clock distribution chip (HMC704X only, not
	AD9516-1). Very fine and well calibrated, but too noisy to be used on
	a sample clock.
\end{itemize}

We plan to use the latter two elements for the scan.

The FPGA then rounds the phase to an integer multiple of sample clock
cycles using previously stored fractional delay data (delay \textless{}-
round(measured - fractional)) and stores the new fractional delay
(fractional \textless{}- measured - delay). It now programs the digital
phase shifters of the slower clocks (FPGA deviceclock and SYSREF) with
the negative of the rounded delay value.

This technique can be implemented on the AD9154 FMC cards, using the
digital delay of the AD9516-1 and IDELAYE3.

\subsection{Sayma RTM clock chip
	connections}\label{sayma-rtm-clock-chip-connections}

The HMC7044 has 14 outputs. They are used for:

\begin{itemize}

	\item
	DAC1 deviceclock
	\item
	DAC1 SYSREF
	\item
	DAC2 deviceclock
	\item
	DAC2 SYSREF
	\item
	ADC1 deviceclock
	\item
	ADC1 SYSREF
	\item
	ADC2 deviceclock
	\item
	ADC2 SYSREF
	\item
	FPGA SYSREF {[}with fine delay{]}
	\item
	FPGA MGT reference clock for DAC
	\item
	FPGA MGT reference clock for ADC
	\item
	additional outputs to FPGA, usable e.g.~if we have problems with the
	recovered RTIO clock.
\end{itemize}

\subsection{Clock constraints}\label{clock-constraints}

\subsubsection{Constraints}\label{constraints}

\begin{itemize}

	\item
	t\_RTIO = n * 1ns
	
	\begin{itemize}

		\item
		period of the coarse RTIO clock
		\item
		n integer to avoid rounding errors and beating between RTIO clock
		and user habit
		\item
		n not necessarily a power of two
		\item
		the same throughout the ARTIQ tree to avoid beating of channels
	\end{itemize}
	\item
	t\_DRTIO\_link = n * 10 * t\_RTIO with n being 1, 2, 4, 8
	
	\begin{itemize}

		\item
		line period of the DRTIO link
		\item
		due to 8b10b and parallel bus width
		\item
		n not a power of two could work but looks impractical.
		\item
		does not need to be the same n for each link
		\item
		AMC backplane links can probably not to 10 GHz line rate but 5 GHz,
		fibers (SFP+) can
	\end{itemize}
	\item
	t\_SAWG\_DATA = t\_RTIO/
\end{itemize}

\begin{verbatim}
f_DAC/f_SAWG: {1, 2, 4, 8}
f_SAWG/f_RTIO: {1, 2, 4, 8}
f_RTIO/f_DRTIO: {10, 20, 40}
f_JESD_P/f_RTIO: {1, 2}
f_JESD/f_JESD_P: {40}
\end{verbatim}

\begin{longtable}[]{@{}lllllll@{}}

	(GHz) & f\_DAC & f\_SAWG & f\_JESD\_P & f\_JESD & f\_RTIO &
	f\_DRTIO\tabularnewline

	\endhead
	A & 2.4 & 0.6 & 0.15 & 6 & 0.15 & 3\tabularnewline
	B & 2 & 1 & 0.25 & 10 & 0.125 & 5\tabularnewline
	C & 0.3 & 0.3 & 0.15 & 6 & 0.15 & 3\tabularnewline

\end{longtable}

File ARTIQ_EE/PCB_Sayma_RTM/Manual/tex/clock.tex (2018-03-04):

\section{Clock distribution mezzanine}

\subsection{Overview}\label{overview}

Clock mezzanines generate high-quality RF/microwave signals for use as
data converter clocks and local oscillators (LOs) by phase-locking
low-noise VCOs to a supplied reference source. They mount on a suitable
carrier, such as \url{Baikal}, which supplies global signals to all RTMs
in a uTCA.4 rack, or to an individual RTM, such as \url{Sayma}, for
local frequency generation.

\subsection{Features and specification}\label{features-and-specification}

\begin{itemize}
	\item
	Reference input from carrier PCB via 2xSMPs, typically 100MHz
	AC-coupled differential 3V3 PECL square-wave.
	\item
	Two independent phase-locked loops (PLLs), one typically used as one
	data converter clock (CLK) and one as a high-frequency reference/local
	oscillator (REF\_LO). Outputs are AC coupled 3V3 PECL square-waves
	provided as differential signals over 2xSMPs.
	\item
	PLL lock indicators accessible via TTLs
	\item
	PLL multiplication factors (output frequencies) accessible from
	carrier via I2C
	\item
	Auxiliary CLK input from MMCX connector on top of PCB with isolated
	ground. Typical input is 50Ohm single-ended, +10dBm. Switching between
	on-board PLL and auxiliary input using integrated ultra-low noise
	clock mux controllable from carrier.
	\item
	Digital/power: copy from AFE specification, and specify pins for PLL
	locked indicators (high-locked) and mux
\end{itemize}

\subsection{Mezzanines}\label{mezzanines}

\subsubsection{Template mezzanine}\label{template-mezzanine}

Used for thermal and electrical testing of carriers, such as Sayma and
Baikal, and as a template for designing clock mezzanines.

The design files are located in
\href{https://github.com/m-labs/sinara/tree/master/ARTIQ_ALTIUM/PCB_mezzanine_clock_template}{ARTIQ\_ALTIUM/PCB\_mezzanine\_clock\_template},
the schematic is
\href{https://github.com/m-labs/sinara/blob/master/ARTIQ_ALTIUM/PCB_mezzanine_clock_template/mezzanine_clock_template.PDF}{here}.

\subsection{Low phase noise clock mezzanine}\label{low-phase-noise-clock-mezzanine}

An ultra-low noise, dual-output fixed-frequency signal generator.

The design files are located in
\href{https://github.com/m-labs/sinara/tree/master/ARTIQ_ALTIUM/PCB_mezzanine_clock}{ARTIQ\_ALTIUM/PCB\_mezzanine\_clock},
the schematic is
\href{https://github.com/m-labs/sinara/blob/master/ARTIQ_ALTIUM/PCB_mezzanine_clock_template/mezzanine_clock_template.PDF}{here}.

Specification:

\begin{itemize}

	\item
	PLL: HMC440
	\item
	VCOs: Crystek CVCO55CC family of narrow-band VCOs
	\item
	Output range for 100MHz input: 400MHz to 3.2GHz, limited by available
	VCOs and HMC440 multiplication factor
	\item
	PLL multiplication factors (output frequencies) fixed by component
	section, but readable from carrier via I2C

\end{itemize}

%\subsubsection{Loop filters}\label{loop-filters}
%
%To do: add component choices and noise models (+ measurements where
%available) for important output frequencies.

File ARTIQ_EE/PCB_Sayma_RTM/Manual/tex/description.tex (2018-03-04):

%\section{Project description}
%	
%The Sayma RTM module extends Sayma AMC board connectivity by DACs and ADCs modules.
%

\section{Functional specifications}

\noindent

\textbf{Programmable resources:}

\begin{itemize}
\item Xilinx Artix-7 XC7A15T-1CSG325

\end{itemize}	

\textbf{Memory:}

\begin{itemize}

	\item EEPROM with MAC and unique ID 
	
\end{itemize}

\textbf{Connectivity:}

\begin{itemize}
	\item 4x mezzaninne connector LSS-120-01-L-DV-A 
	\item 40x SMP connector for ADC/DAC
%	\item Stand-alone 12V power connector 
	\item RTM connector with 16 GTP pair routed to it.
	\item GTP on RTM connector connected to:
	\begin{itemize}
		\item DAC x16 [Tx]
		\item ADC x8 [Rx]
		\item FPGA MGT 2x2 [Tx + Rx]
		\item SATA x2 
	\end{itemize}
	\item uRFB connector
	
\end{itemize}

\textbf{Supply:}

\begin{itemize}
	\item Monitoring of voltage and Power supply for FPGA and P3V3
	
\end{itemize}

\textbf{Clocking:}

\begin{itemize}
	\item UFL CLK input
	\item SMA CLK output
	\item Si5324 Clock recovery
	
\end{itemize}

\textbf{Other:}

\begin{itemize}
	\item Temperature, voltage and current monitoring for critical power buses

\end{itemize}

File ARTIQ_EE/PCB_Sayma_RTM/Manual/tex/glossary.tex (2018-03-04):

\section{Glossary}

\begin{description}
	\item[AFE] Analogue front-end.
	\item[AMC Module or Modul] An AMC Module is a mezzanine or modular add-on card that extends the
	functionality of a Carrier Board. The term is also used to generically refer to the
	different varieties of Multi-Width and Multi-Height Modules.
	\item[BaseMod] Base-band input/output mezzanine.
	\item[COTS] Commercial off-the-shelf. Product which is designed and can be easily purchased.
	\item[EEM] Eurocard Extension Module is a Sinara standard for low-cost, low-bandwidth peripherals that are controlled by ARTIQ DRTIO.
	\item[Fat Pipes] Ports 4 though 11 of the AMC Connector constitute the Fat Pipes Region. This
	Region of Ports is intended for the assignment of multiple Lane interfaces, also
	called “fat pipes”. Fat Pipe 1 [Ports 4-7], Fat Pipe [Ports 8-11].
	\item[FMC] FPGA Mezzanine Card
	\item[HEPP] High Energy \& Particle Physics.
	\item[Hot Swap] To remove a component (e.g., an AMC Module) from a system (e.g., an AMC Carrier
	AdvancedTCA Board) and plug in a new one while the power is still on and the
	system is still operating.
	\item[IPMB] ntelligent Platform Management Bus. The lowest level hardware management bus
	as described in the Intelligent Platform Management Bus Communications Protocol
	Specification.
	\item[Management Power or MP] The 3.3V power for a Module's Management function, individually provided to each Slot by the Carrier
	\item[MGT] Multi-Gigabit Transceiver.	
	\item[MixMod] An up-converting mezzanine, using an analogue IQ mixer to mix the input and output RF signals with a LO supplied by Sayma.
	\item[MMC] Module Management Controller. The MMC is the required intelligent controller that
	manages the Module and is interfaced to the Carrier via IPMB-Local.
	\item[RFBP] RF Backplane.
	\item[RTM] Rear Transition Module.
	\item[Sayma] Smart Arbitrary Waveform Generator, providing 8 channels of 1.2 GSPS 16-bit DACs (2.4 GHz DAC clock) and 125 MSPS 16-bit ADCs. It consists of an AMC, providing the high-speed digital logic, and a RTM, holding the data converters and analog components.
	\item[Sianra] Open-source hardware ecosystem originally designed for use in quantum physics experiments running the ARTIQ control software. It is licensed under CERN OHL v1.2.
	\item[uTCA] Micro Telecommunications Computing Architecture. MicroTCA is a modular, open standard for building high performance computer systems in a small form factor.
\end{description}

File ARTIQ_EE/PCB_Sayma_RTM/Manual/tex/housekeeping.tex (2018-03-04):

\section{Housekeeping Signals}

\subsection{sensors}
Temperature:\\

\begin{longtable}{|c|c|c|c|c|}\hline
	\multicolumn{5}{|c|}{IPMI\_I2C}\\ \hline
	No & Addr. & placement & Type & Accuracy \\ \hline
	IC39 & 0x4A & Bottom - close to ADC  & LM75 & +/- 2 \\ \hline
	IC40 & 0x49 & Bottom - close to HMC7043 buffer& LM75 & +/- 2  \\ \hline
	IC44 & 0x24 & Bottom - under Mezzanine1 & MAX664A & +/- 1 \\ \hline
\end{longtable}

\begin{longtable}{|c|c|c|c|c|}\hline
		\multicolumn{5}{|c|}{TEMP\_SENS\_I2C}\\ \hline
	No & Addr. & placement & Type & Accuracy \\ \hline
	IC56 & 0x48 & Bottom - under DAC & ADT7420 & +/- 0.25 \\ \hline
	IC57 & 0x49 & Bottom center & ADT7420 & +/- 0.25  \\ \hline
\end{longtable}

All sensors are available either from AMC siede I2C or from RTM\_FPGA.
%All temperature sensors are tied tohether to one I2C bus - I2C\_SENS. \\

\subsection{Safety interlocks}

Temperature interlock is available on RTM board only and gets activated after reaching 80 degrees. This is hardware interlock and cannot be deactivated. Dedicated LED (LD15) gets on and RTM power supply is off until the temperature is exceeded

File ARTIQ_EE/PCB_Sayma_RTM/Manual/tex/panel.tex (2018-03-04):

\section{LEDs, ICs and headers}

		\begin{figure}[htbp!]
			\centering
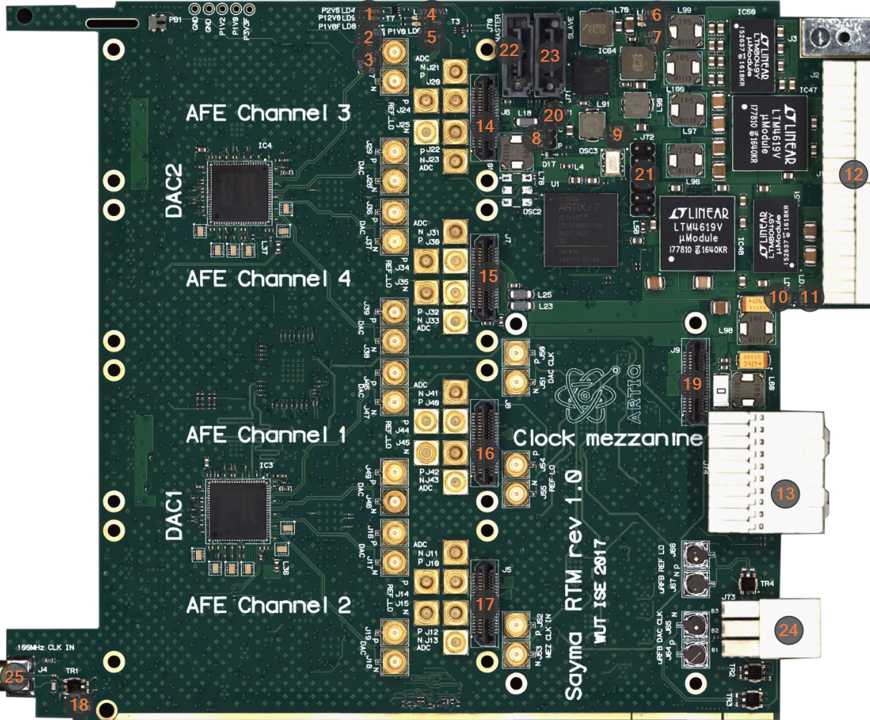
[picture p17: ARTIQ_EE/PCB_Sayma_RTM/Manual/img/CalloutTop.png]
			\\
			\caption{Top view}
		\end{figure}
		
		\begin{figure}[htbp!]
			\centering
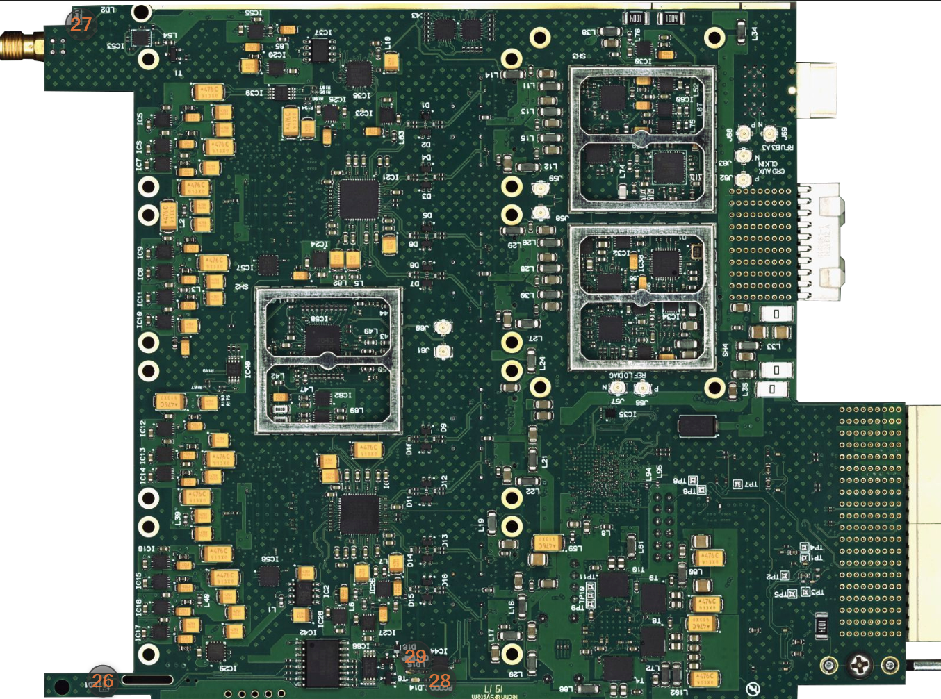
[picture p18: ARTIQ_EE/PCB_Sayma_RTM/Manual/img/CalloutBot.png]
			\\
			\caption{Bottom view}
		\end{figure}
\clearpage

\begin{longtable}{|c|c|c|} \hline
	\multicolumn{3}{|c|}{Call out table } \\ \hline	
	Call out & Designator & Description \\ \hline
	12 & J2 & RTM Connector \\ \hline
	13 & J74 & uRFB Connector \\ \hline
	14 & J76 & Mezzanine 1 Connector \\ \hline
	15 & J76 & Mezzanine 2 Connector \\ \hline
	16 & J76 & Mezzanine 3 Connector \\ \hline
	17 & J76 & Mezzanine 4 Connector \\ \hline	
	19 & J9 & CLK Mezzanine Connector\\ \hline
	20 & W1 & EXAR I2C header \\ \hline
	21 & J72 & Header with I/Os see Figure \ref{ios} \\ \hline
	22 & J70 & Master SATA  \\ \hline
	23 & J71 & Slave SATA \\ \hline
	24 & J73 & uRFB Conenctor \\ \hline
	25 & J4 & SMA, EXT 100 MHz input \\ \hline

\end{longtable}

Callout 18: U2 is
\begin{itemize}
	\item off if RTM is ok 
	\item red if RTM is in an error state
\end{itemize}

Callout 26: LD2 is
\begin{itemize}
	\item off if - user defined
	\item green if - user defined
\end{itemize}

Callout 27: LD1 is
\begin{itemize}
	\item off if RTM has initialized in crate
	\item blue if  power is cut off and is possible to remove the board
\end{itemize}

Callout 28: LD14 is
\begin{itemize}
	\item off if there is a problem with power converters
	\item green if all power chips send Power Good
\end{itemize}

Callout 25: LD15 is
\begin{itemize}
	\item off if RTM is ok
	\item green if RTM reach 80 degrees (power is cut off)
	\end{itemize}

\begin{longtable}{|c|c|c|c|c|c|c|} \hline
		\multicolumn{7}{|c|}{Power LED table }\\ \hline
	Call out & Designator & Description&  Colour &nominal state& IC &Failure\\ \hline
	1 & LD4 & P2V0 & Green & on & Power & off \\ \hline
	2 & LD9 & P12V0 & Green & on & Power & off \\ \hline 
	3 & LD8 & P1V8 & Green & on & Power & off \\ \hline 
	4 & LD7 & P1V2 & Green & on & Power & off \\ \hline 
	5 & LD6 & P1V0 & Green & on & Power & off \\ \hline 
	6 & LD16 & P12V0A & Green & on & Power & off \\ \hline 
	7 & LD10 & N12V0A & Green & on & Power & off \\ \hline 
	8 & LD17 & P3V3 & Green & on & Power & off \\ \hline 
	9 & LD3 & P4V0 & Green & on & Power & off \\ \hline 
	10 & LD5 & P6V0A & Green & on & Power & off \\ \hline  	
	11 & LD12 & N6V0A & Green & on & Power & off \\ \hline  		 
\end{longtable}

\subsection{Headers pinout}

		\begin{figure}[htbp!]
			\centering
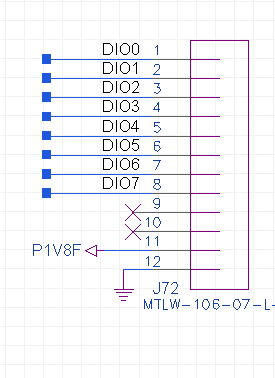
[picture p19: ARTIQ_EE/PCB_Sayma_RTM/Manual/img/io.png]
			\\
			\caption{DIO - Call out 21} \label{ios}
		\end{figure}
%
%		\begin{figure}[htbp!]
%			\centering
%			\includegraphics[width=9cm]{img/jtaglpc.png}\\
%			\caption{JTAG - Call out  21}
%		\end{figure}
%		
%		\begin{figure}[htbp!]
%			\centering
%			\includegraphics[width=9cm]{img/gpio.png}\\
%			\caption{DIO - Call out 23}
%		\end{figure}

\clearpage

%\begin{longtable}{|c|c|c|} \hline
%		\multicolumn{3}{|c|}{Tespoints table}\\ \hline
%	TPx & Sig Name & LPC pin \\ \hline
%	TP1 & MII1\_col & C13 \\ \hline
%	TP2 & SDCLK & J10 \\ \hline
%	TP3 & SDCMD & K14 \\ \hline
%	TP4 & SDPWR & K11 \\ \hline
%	TP5 & SDDAT0 & L14 \\ \hline
%	TP6 & SDDAT1 & M12 \\ \hline
%	TP7 & SDDAT2 & N14 \\ \hline
%	TP8 & SDDAT3 & M11 \\ \hline
%	
%\end{longtable}	

\subsection{Location ICs}

		\begin{figure}[htbp!]
			\centering
			\\
			\caption{Top}
		\end{figure}
		\begin{figure}[htbp!]
			\centering
			\\
			\caption{Bottom}
		\end{figure}
\clearpage

\begin{longtable}{|c|c|c|} \hline
		\multicolumn{3}{|c|}{ICs Location}\\ \hline	
	Ux & IC & Description \\ \hline
	U1 & Artix-7 & FPGA \\ \hline
	IC1/IC43	&	TCA9548		& I2C MUX 			\\	\hline	
	IC3 & AD9154 & DAC1 \\ \hline
	IC4 & AD9154  & DAC2\\ \hline
	IC5/IC6/IC7	&	LT3045		&  	DAC supply		\\	\hline
	IC8/IC9/IC10/IC11	&	LT3045		&  	DAC supply		\\	\hline	
	IC12/IC13/IC14 & LT3045 & DAC supply \\ \hline
	IC15/IC16/IC17/IC18 & LT3045 & DAC supply \\ \hline	
	IC20	&	LT3045		&  DAC supply			\\	\hline	
	IC21	&	AD9656		&  	ADC		\\	\hline
	IC22 & AD9656 & ADC \\ \hline
	IC29 & ADP1740 & P1V8 LDO \\ \hline	
	IC32 &	LT3045 & Si5324 power supply \\ \hline
	IC33 & ADM7151 & P5V0 LDO \\ \hline
	IC36	&	AD7194		& ADC 			\\	\hline
	IC37	&	ADR440		&  ADC reference			\\	\hline
	IC38 & Si5324 & Clock recovery \\ \hline	
	IC39 & LM75 & Temp sens \\ \hline
	IC40 & LM75 & Temp sens \\ \hline	
	IC42 & PCF8574 & I2C to GPIO extender \\ \hline	
	IC44 & MAX6642 & Temp sens \\ \hline
	IC45	&	ADCLK948		&  Clock buffer		\\	\hline
	IC46	&	ADCLK948		& Clock buffer 		\\	\hline					
	IC47 & LTM4619 & Buck converter P2V0 and P4V0\\ \hline
	IC48 & TPS 74401  & Buck converter P6V0\\ \hline
	IC50 &  LTM8049 & Buck converter P12V0A and N12V0A \\ \hline
	IC51 & LTM8049& Buck converter N6V0A \\ \hline
	IC52 & ADCLK948 & Clock buffer \\ \hline
	IC54 &ADCLK948 & Clock buffer \\ \hline	
	IC53	&	LTC6957		&  Isolation external clock input			\\	\hline	
	IC55	&	LT3045		&  DAC supply			\\	\hline	
	IC56 & ADT7420 & Temp sens \\ \hline
	IC57 & ADT7420 & Temp sens \\ \hline
	IC58	&	HMC7043		&  	Clock buffer		\\ \hline
	IC59	&	HMC830		&  	Clock buffer		\\	\hline
	IC62/IC63		& LT3045	& HMC7043 power supply	\\ \hline			
	IC64 & XR77129 & EXAR \\ \hline
	IC66 & AT24MAC402 & EEPROM \\ \hline
	T4/T8/T9/T10 & FDMS7608S & Exar transistors\\ \hline

\end{longtable}

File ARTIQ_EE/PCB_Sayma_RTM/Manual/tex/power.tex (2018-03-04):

\section{Power}
\subsection{Power supply}
The card can operate connested to SAYMA AMC card. When the card is inserted to the SAYMA AMC,  the power is applied from RTM connector -J2, +12V (4 power lines) and +3.3\_MP(1 line). Both voltages can be controlled by SAYMA AMC.
+12 is converted to lower voltages and negative voltages, simplified power map is in figure \ref{powermap}. There are few types of power distributors, fixed LDOs, Buck converters and Exar chip - quad channel digital Pulse Width Modulated (PWM) step down (buck) controller. Exar allows for adjust power parameters and for set particular power oorder. Exar firmware monitors current and responds if its too high.  Additionaly all LDOs have connected PowerGood outputs so it is possible to read the proper state of all power busses. 

\todo[inline]{TBD voltage noise}

%Maximum board(AMC+RTM module) power consumption estimate to 3A @ 12V.\\
%
%	\textit{\textbf{Note:} Please note that power consumption mostly depends from FPGA configuration. \\}

\begin{itemize}

\item Input voltage range: 10.8-13.2 [V]\\
\item The board needs active cooling. Approx. 20CFM in 20 C air.\\

\end{itemize}

Exar chips are configured via EXAR\_I2C bus (I2CMUX7) or directly by connecting to W1 
%(call-out 28) 
header. For proper configuration \textbf{Exar Power Architect} in version \textbf{5.2-r1} is needed.
% Configuration files can be found at github in folder \href{https://github.com/m-labs/sinara/tree/master/EXAR\_config}{m-labs/sinara/Exar\_config}\\

\noindent
\textbf{Exar Power Archtect 5.2-r1:}
\href{https://www.exar.com/content/document.ashx?id=21632}{https://www.exar.com/content/document.ashx?id=21632}\\
\textbf{Configuration files:}
\href{https://github.com/m-labs/sinara/tree/master/EXAR\_config}{https://github.com/m-labs/sinara/tree/master/EXAR\_config}\\
\textbf{Datasheet:}\href{https://www.exar.com/ds/xr77129_1a_120514.pdf}{https://www.exar.com/ds/xr77129\_1a\_120514.pdf}\\
\textbf{Quick Start Guide:} \href{https://www.exar.com/files/powerxr/PA5-QSG_110_010614.pdf}{https://www.exar.com/files/powerxr/PA5-QSG\_110\_010614.pdf}\\

Actual voltages and current consumption, temperature can be found in Chip Dashboard. There is also oportunity to adjust settings.

\begin{figure}[htbp!]
	\centering
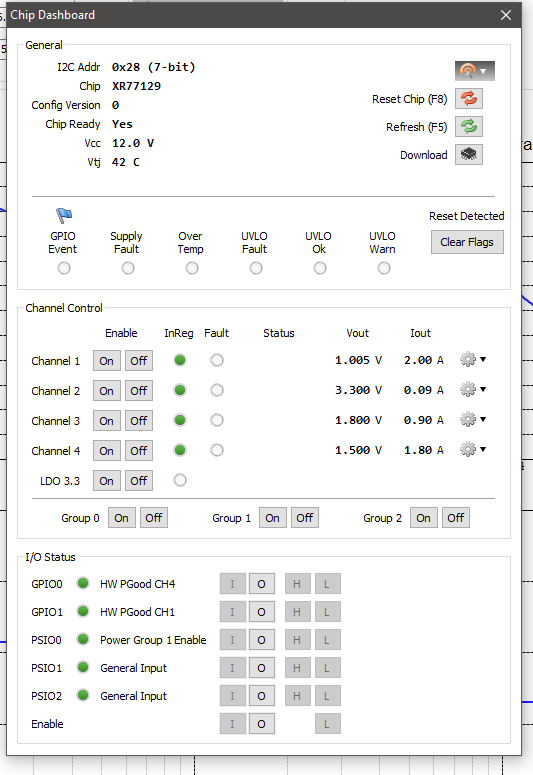
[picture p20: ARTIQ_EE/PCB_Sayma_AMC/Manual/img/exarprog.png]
	\\
	\caption{Chip Dashboard} 
\end{figure}

\clearpage
\subsection{Power configuration} 

\subsubsection{Power map}

	\begin{figure}[htbp!]
		\centering
		\\
		\caption{Power map} \label{powermap}
	\end{figure}

\begin{longtable}{|c|c|c|} \hline
\multicolumn{3}{|c|}{voltages and currents}	\\ \hline
P1V0 & 1.0V & 4A \\ \hline
P1V2 & 1.2V & 2A\\ \hline
P1V8 & 1.8V & 2A\\ \hline
P2V0 & 2.0V & 4A\\ \hline
P3V3 & 3.3V & 4A\\ \hline
P4V0 & 4.0V & 4A\\ \hline
P6V0 & 6.0V & 8A\\ \hline
P12V0A & 12.0V & 1A \\ \hline
N6V0A & -6.0V & 4A\\ \hline
N12V0A & -12.0V & 1A \\ \hline

\end{longtable}
	
\subsubsection{Exar parameters}

Exar chip(XR77129) has 4 configurable outputs with configirable current limits. Each channel can be confugured individually. It is possible to set voltage, current limit and power sequencing. In Figure \ref{exar1} we can see that main power supply is 12V, Under Voltage Lockout(UVLO) is set to 6V, so below this value chip will shutdown all channels. When the temperature rise under Over Temperature Protection (OTP) 105 degrees, the chip will generate warning event and restart. \\
All 4 channells can be grouped together and will start-up and shut-down in an user defined sequwnce. Selecting none means channels will not be assigned to any group and therefore, will be controlled independently. Group 0 is controlled by ENABLE or EXAR\_I2C command. Group 1 can be controlled by GPIO or by EXAR\_I2C command. By selecting 'Wait PGOOD' next channel will not power up untill current channel reaches the target level. Delay is an additional delay time which postpone after power up one and another channel in group.\\
In on-going Exar configuration - Figure \ref{exar2}, power sequencing looks like this: After Enable - EN\_DC\_DC, P1V0 start-up, after it reaches proper value, Exar turn ramp up another channel in this group - P3V3. In the same order are ramp up next two channels in this group.

	\begin{figure}[htbp!]
		\centering
		\\
		\caption{Exar configuration} \label{exar1}
	\end{figure}
\clearpage	
	\begin{figure}[htbp!]
		\centering
		\\
		\caption{Exar power on delays} \label{exar2}
	\end{figure}	

%\subsubsection{Exar configuration}
%Exar chips are configured via I2C bus (MUX Port 5) or directly by connecting to W1 (call-out 28) header. For proper configuration \textbf{Exar Power Architect} in version \textbf{5.2-r1} is needed.
%% Configuration files can be found at github in folder \href{https://github.com/m-labs/sinara/tree/master/EXAR\_config}{m-labs/sinara/Exar\_config}\\
%
%\noindent
%\textbf{Exar Power Archtect 5.2-r1:}
%\href{https://www.exar.com/content/document.ashx?id=21632}{https://www.exar.com/content/document.ashx?id=21632}\\
%\textbf{Configuration files:}
%\href{https://github.com/m-labs/sinara/tree/master/EXAR\_config}{https://github.com/m-labs/sinara/tree/master/EXAR\_config}\\
%\textbf{Datasheet:}\href{https://www.exar.com/ds/xr77129_1a_120514.pdf}{https://www.exar.com/ds/xr77129\_1a\_120514.pdf}\\
%\textbf{Quick Start Guide:} \href{https://www.exar.com/files/powerxr/PA5-QSG_110_010614.pdf}{https://www.exar.com/files/powerxr/PA5-QSG\_110\_010614.pdf}\\
%
%
%Actual voltages and current consumption, temperature can be found in Chip Dashboard. There is also oportunity to adjust settings.
%
%	\begin{figure}[htbp!]
%		\centering
%		\includegraphics[scale=0.6]{img/exarprog.png}\\
%		\caption{Chip Dashboard} 
%	\end{figure}
%
\subsection{Maximum power draw for each Mezzaninne}

\begin{longtable}{|c|c|} \hline
	Power rail[V] & Current [mA]\\ \hline
	+12 & 200 \\ \hline
	-12 & 50 \\ \hline
	+6 & 1500 \\ \hline
	-6 & 100 \\ \hline
	+3.3 & 1000 \\ \hline
	
\end{longtable}

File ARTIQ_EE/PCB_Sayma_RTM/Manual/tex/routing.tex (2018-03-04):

\section{Routing}
This section contain general blockm scheme of SAYMA RTM board and I2C map with addresses. General Block Scheme -figure \ref{BlockScheme}
shows more important connections between components. I2C connections with addresses can be found in figure \ref{I2C}.
	\begin{figure}[htbp!]
		\centering
		\\
		\caption{Block Scheme} \label{BlockScheme}
	\end{figure}
\clearpage
The I2C MUX is made from two (TCA9548ARGER)  I2C multiplexers. In Sayma AMC there are two main I2C busses: MMC\_I2C and FPGA\_I2C. Each of them is connected to one multiplexer. Outputs are tied together, so Masters (MMC and FPGA) can acces to any of 7 I2C busses. Addidtionaly MMC has acces to FPGA\_I2C and is connected to IPMB through AMC connector.\\  
	\begin{figure}[htbp!]
		\centering
		\\
		\caption{I2C} \label{I2C}
	\end{figure}

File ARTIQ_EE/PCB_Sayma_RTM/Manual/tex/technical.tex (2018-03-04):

\section{PCB technical information}

\href{https://github.com/m-labs/sinara/tree/master/ARTIQ_EE/PCB_Sayma_RTM/Output}{Project outputs}

Stackup:

\begin{longtable}{|c|c|l|}\hline
Layer& Copper&	Function \\ \hline
L1& 36 &	polygons, short traces and analog signals between ADC/DAC and connectors\\ \hline
P2&	18 &GND\\ \hline
L3&	18 &high speed signals, LVDS, GTX, clocks\\ \hline
P4&	18& GND\\ \hline
L5&	18&hig speed, LVDS< GTX, clocks, vertical slow control\\ \hline
P6&	18&GND\\ \hline
L7&	18&non-critical signals like I2C, SPI, mezzanine IOs, status, LED, some pwoer polygons, etc\\ \hline
P8&	18&GND\\ \hline
P9&	18&split power plane\\ \hline
L10&36&	short signal layers (ADCs), mainly polygons and short traces (EMI mitigation)\\ \hline
\end{longtable}
The total height of the board is: 1.59mm 
Laminat is a standard FR4.

	\begin{figure}[htbp!]
		\centering
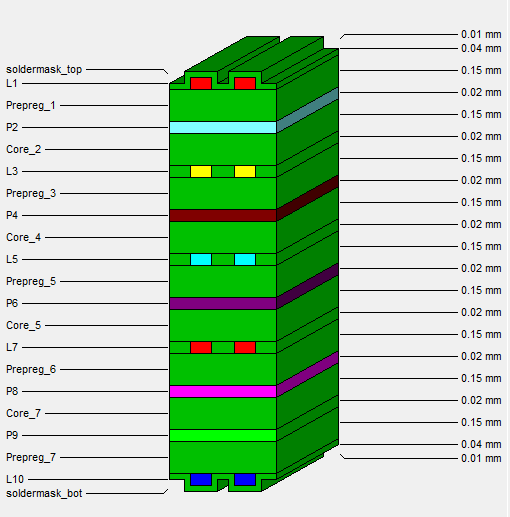
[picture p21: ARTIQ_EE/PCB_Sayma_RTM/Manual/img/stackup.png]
		\\
		\caption{SAYMA RTM stackup}
	\end{figure}
	
\textit{\textbf{Note:}The thickness of copper in Figure 17 is 0.04mm and 0.02mm is due to approximation. In fact it is 0.036mm and 0.018mm.}

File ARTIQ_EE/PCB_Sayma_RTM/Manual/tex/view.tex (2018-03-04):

\section{Product view}	
	
	\begin{figure}[htbp!]
		\centering
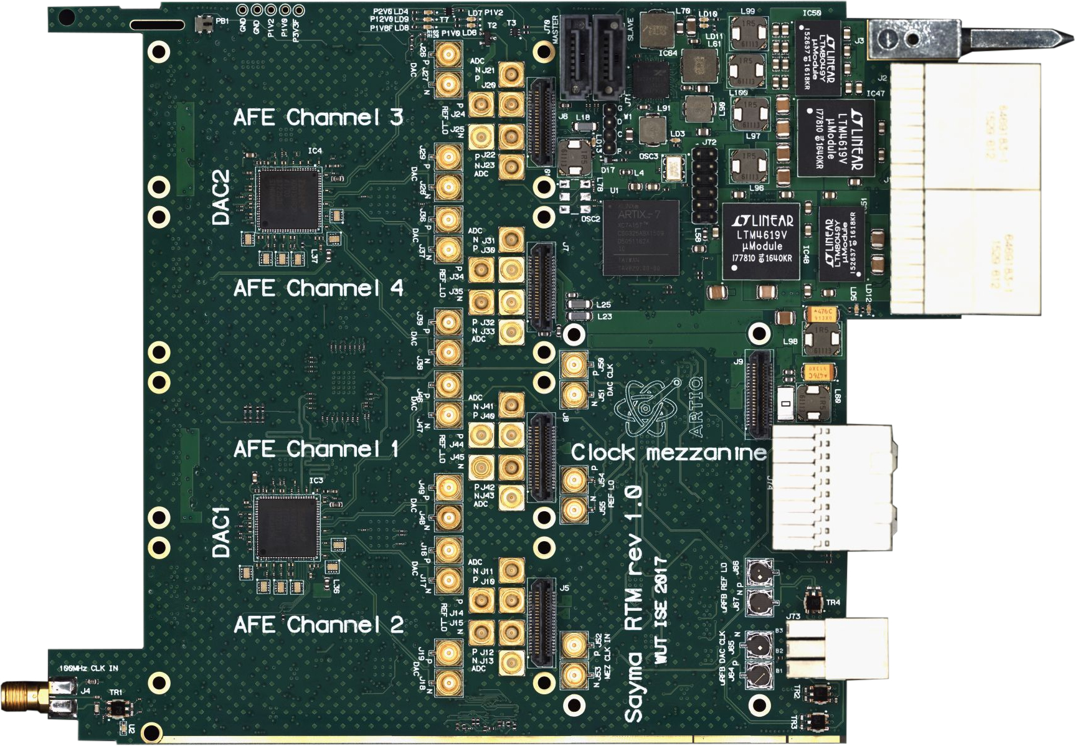
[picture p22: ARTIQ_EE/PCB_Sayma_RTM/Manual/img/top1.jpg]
		\\
		\caption{Top view}
	\end{figure}
	
		\begin{figure}[htbp!]
			\centering
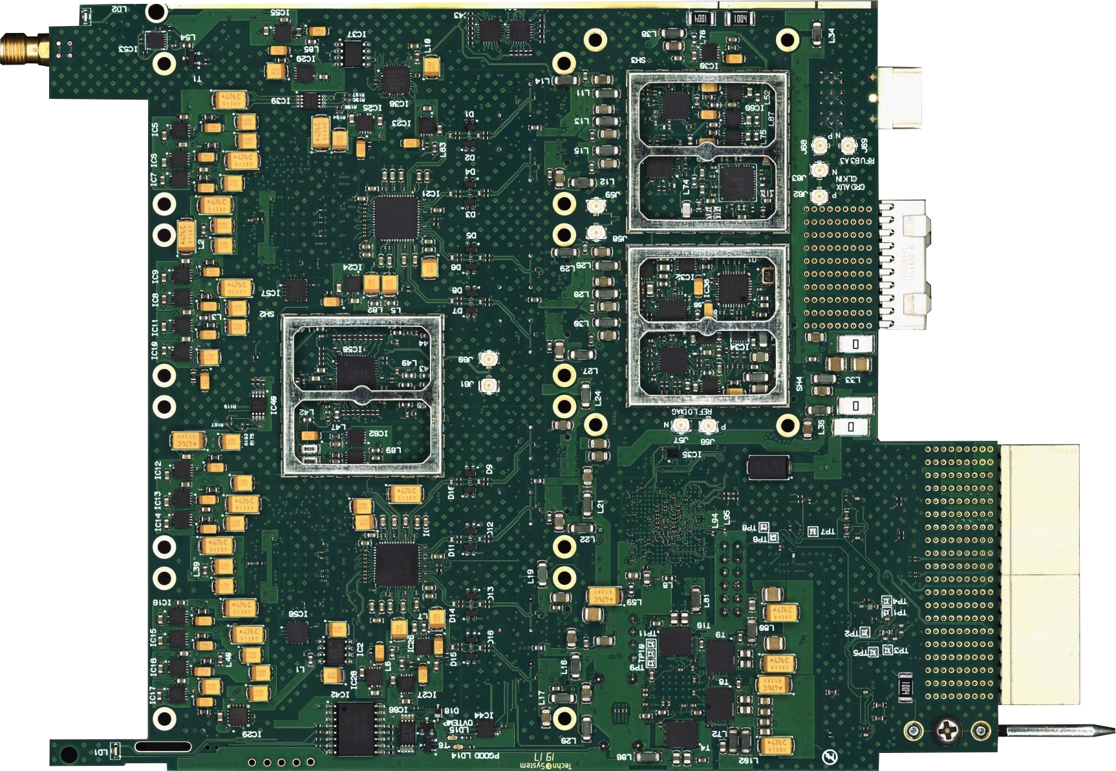
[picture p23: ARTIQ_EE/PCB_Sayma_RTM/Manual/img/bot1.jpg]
			\\
			\caption{Bottom view}
		\end{figure}

%		\begin{figure}[htbp!]
%			\centering
%			\includegraphics[width=17cm]{img/front.jpg}\\
%			\caption{Front view}
%		\end{figure}
%

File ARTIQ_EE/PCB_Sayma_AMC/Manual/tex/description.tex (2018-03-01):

%\section{Project description}
%	
%The Sayma AMC is a Advanced Mezzanine Card carrier board to carry FMC cards and connect RTM modules.
%
%	

\section{Functional specifications}

\noindent

\textbf{Programmable resources:}

\begin{itemize}
\item Xilinx Kintex UltraScale – XCKU040-1FFVA-1156C    FPGA
	\begin{itemize}
		\item speed grade: -1
		\item 20 GTH transceivers (Max Preformance 16.3 Gb/s)
	\end{itemize}
\item MMC: LPC17762984
\end{itemize}	

\textbf{Memory:}

\begin{itemize}
	\item 512Mb  DDR3 SDRAM (32-bit interface), 800MHz (clock)
	\item 1Gb  DDR3 SDRAM (64-bit interface), 800MHz (clock)
	\item SPI Flash for FPGA configuration. Accessible by MMC
	\item SPI Flash for user data storage
	\item EEPROM with MAC and unique ID 
	
\end{itemize}

\textbf{Connectivity:}

\begin{itemize}
	\item 1 high pin count (HPC) FMC slot for single width mezzanine card
	\item Micro-USB UART connected to FPGA or MMC
	\item Stand-alone 12V power connector 
	\item MGT (Multi-Gigabit Transceiver) connected to:
	\begin{itemize}
%		\item FMC x1
		\item RTM x16
		\item Fat\_Pipe1 x2
%		\item AMC P2P x4
%		\item Port 0 – possibility connected to SATA
		\item SFP x2
	\end{itemize}
%	\item RTM connector with 8 GTP routed to it. Compatible with Sayma RTM module.
	\item  Port 0 – possibility connected to SATA
	\item RTM connector compatible with Sayma RTM module
	
\end{itemize}

\textbf{Supply:}

\begin{itemize}
	\item Monitoring of voltage and Power supply for RTM 12V and FMC 12V
	\item FMC VADJ fixed to 1V8
	\item Monitoring current of all FMC buses
	\item Stand-alone power connectore
%	\item Czy Exar monitoruje powera? 
	
\end{itemize}

\textbf{Clocking:}

\begin{itemize}
	\item Clock recovery Si5324
	\item UFL CLK input
	\item SMA CLK output

\end{itemize}

\textbf{Other:}

\begin{itemize}
	\item Temperature, voltage and current monitoring for critical power buses
	\item Temperature monitoring: FMC1, supply, FPGA core, DDR memory
	\item JTAG multiplexer (SCANSTA) for FMC access, local JTAG port and remote debug/Chipscope via Ethernet
	
\end{itemize}

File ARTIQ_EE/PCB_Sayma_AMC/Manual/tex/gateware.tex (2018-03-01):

\section{Gateware configurations}
\todo[inline]{mathrm problem}
\paragraph{Spline parametrization}\label{spline-parametrization}

\emph{This is inherited from the
	\href{http://pdq2.readthedocs.io/en/latest/}{pdq2 documentation}}

The method of compression is a polynomial basis spline (B-spline). The
data consists of a sequence of knots. Each knot is described by a
duration \texttt{\$\textbackslash{}Delta\ t\$} and spline coefficients
\texttt{\$u\_\{n\}\$} up to order \texttt{\$k\$}. If the knot is
evaluated starting at time \texttt{\$t\_\{0\}\$}, the output
\texttt{\$u(t)\$} for
\texttt{\$t\textbackslash{}in{[}t\_\{0\},t\_\{0\}+\textbackslash{}Delta\ t{]}\$}
is
\texttt{\$\$u(t)=\textbackslash{}sum\_\{n=0\}\^{}\{k\}\textbackslash{}frac\{u\_\{n\}\}\{n!\}(t-t\_\{0\})\^{}\{n\}=u\_\{0\}+u\_\{1\}(t-t\_\{0\})+\textbackslash{}frac\{u\_\{2\}\}\{2\}(t-t\_\{0\})\^{}\{2\}+...\$\$}
A sequence of such knots describes a spline waveform. From one discrete
time \texttt{\$i\$} to the next \texttt{\$i+1\$} each accumulator
\texttt{\$v\_\{n,i\}\$} is incremented by the value of the next higher
order accumulator: \texttt{\$\$v\_\{n,i+1\}=v\_\{n,i\}+v\_\{n+1,i\}\$\$}
For a cubic spline the mapping between accumulators' initial values
\texttt{\$v\_\{n,0\}\$} and the polynomial derivatives or spline
coefficients \texttt{\$u\_\{n\}\$} can be done off-line and must take
into consideration the finite time step size
\texttt{\$\textbackslash{}tau\$}. The data for each knot is described by
the integer duration
\texttt{\$T=\textbackslash{}Delta\ t/\textbackslash{}tau\$} and the
initial values \texttt{\$v\_\{n,0\}\$}. This representation allows both
transient large-bandwidth waveforms and slow but smooth large duty cycle
waveforms to be described very efficiently.

\paragraph{Waveform parametrization}\label{waveform-parametrization}

The gateware will support at least 8 independent channels.

Each channel emits waveforms of the general parametrization:
\texttt{\$\$z=\textbackslash{}left(\ a\_1e\^{}\{i(f\_1\ t+p\_1)\}\ +\ a\_2e\^{}\{i(f\_2\ t+p\_2)\}\textbackslash{}right)e\^{}\{i(f\_0t+p\_0)\}\$\$}
\texttt{\$\$o=u+b\_0\textbackslash{}mathrm\{Re\}(z)+b\_1\textbackslash{}mathrm\{Im\}(z\^{}\textbackslash{}prime)\$\$}

\begin{itemize}
	\item
	\texttt{\$o\$} is the (real valued) output of a channel
	\item
	\texttt{\$z\$} is the complex-valued output of the ``generator''
	associated with each channel
	\item
	\texttt{\$z\^{}\textbackslash{}prime\$} is the complex-valued output
	from the generator of each channel's ``buddy'' channel. Two adjaccent
	channels form a buddy pair. This enables seamless usage of the complex
	data path features in DACs, complex (IQ) analog modulation, and yields
	``four-tone'' support on IQ channels for free.
	\item
	\texttt{\$u\$} and \texttt{\$a\$} are 16-bit cubic (third order)
	spline interpolators
	\item
	\texttt{\$p\$} are 16-bit constant (zeroth order) spline interpolators
	\item
	\texttt{\$f\$} are 48-bit linear (first order) interpolators
	\item
	\texttt{\$b\$} are switches (\texttt{\$1\$} or \texttt{\$0\$})
\end{itemize}

\paragraph{Datapath details}\label{datapath-details}

\begin{itemize}
	\item
	\texttt{\$f\_\textbackslash{}mathrm\{DATA\}\textbackslash{}geq1\textbackslash{},\textbackslash{}mathrm\{GHz\}\$}.
	Exact clock speed is TBD and depends on simultaneously meeting
	hardware constraints and an integer relationship with the RTIO clock
	and physics/noise requirements.
	\item
	Oscillator \texttt{\$f\_0,p\_0\$} is sampled at
	\texttt{\$f\_\{DATA\}\$}
	\item
	Interpolators are updated and interpolate at
	\texttt{\$f\_\textbackslash{}mathrm\{DATA\}/k\$} with \texttt{\$k\$}
	typically 4 or 8 and
	\texttt{\$f\_\textbackslash{}mathrm\{DATA\}/k\ \textbackslash{}geq\ 125\textbackslash{},\textbackslash{}mathrm\{MHz\}\$}
	\item
	Oscillators \texttt{\$f\_\{1,2\},p\_\{1,2\}\$} are sampled at
	\texttt{\$f\_\{DATA\}/k\$}
	\item
	All amplitude summing junctions shall implement saturating summation
	to prevent wrap-around.
	\item
	All amplitude summing junctions shall implement configurable and
	guaranteed gateware low-high limiters.
	\item
	All amplitude summing junctions shall register saturation events.
	\item
	To up-sample the data from the \texttt{\$f\_1\$},\texttt{\$f\_2\$}
	oscillators by \texttt{\$k\$} before passing it into the
	\texttt{\$f\_0\$} oscillator, a CIC filter of order TBD shall be
	implemented for anti-aliasing. CIC filters are linear phase.
	\item
	To implement further anti-aliasing, a symmetric (thus linear phase)
	FIR filter with TBD taps (FPGA DSP resource limits) shall be
	implemented after the CIC filter.
	\item
	All spline interpolators and the total channel output shall be
	monitored by the ARTIQ channel monitoring infrastructure.
	\item
	All spline interpolators shall support ARTIQ injection/override.
\end{itemize}

\paragraph{Clocking and
	synchronization}\label{clocking-and-synchronization}

\begin{itemize}
	\item
	Timestamps for spline knot scheduling are at least 62 bit wide.
	\item
	Spline knots have 16-bit dynamic range in time.
	\item
	In order to support slower sweeps with sparser spline knots, the
	dynamic range of the spline coefficients can be extended using time
	stretcher. It decelerates the spline evolution/interpolation rate by a
	factor of \texttt{\$2\^{}E\$}.
	\item
	Waveform output shall be with deterministic latency with respect to
	the RTIO clock:
	
	\begin{itemize}
		\item
		across channels on the same card (to within DAC chip specification)
		\item
		across cards in the same rack (to within DAC chip and intra-rack
		DRTIO clock sycnchronization)
		\item
		across racks controlled by the same core device (to within DAC chip
		and DRTIO clock synchronization)
	\end{itemize}
	\item
	Each card can be clocked by an internal DAC clock derived from the
	RTIO clock or by an external DAC clock.
	\item
	When an external DAC clock is used, the waveform synchronization is
	ensured to within one DAC clock cycle (or the limit of the DAC chip
	whichever is higher) but below that depends on the phase of the
	external DAC clock.
	\item
	All spline knot interpolators can be updated independently (and also
	simultaneously) of each other.
	\item
	All spline interpolator latencies from the internal ``RTIO clock
	reference plane'' to the DAC output are matched and deterministic.
	Channel and board latencies are matched and deterministic (see above).
	\item
	Minimum spline knot duration is
	\texttt{\$k/f\_\textbackslash{}mathrm\{DATA\}\$}.
\end{itemize}

\paragraph{Phase update modes}\label{phase-update-modes}

The phase accumulator of the DDS cores can be updated in multiple
different modes during a phase and/or frequency update.

\begin{itemize}
	\item
	relative phase update:
	\texttt{\$q\^{}\textbackslash{}prime(t)\ =\ q(t\^{}\textbackslash{}prime)\ +\ (p\^{}\textbackslash{}prime\ -\ p)\ +\ (t\ -\ t\^{}\textbackslash{}prime)\ f\^{}\textbackslash{}prime\$}
	\item
	absolute phase update:
	\texttt{\$q\^{}\textbackslash{}prime(t)\ =\ p\^{}\textbackslash{}prime\ +\ (t\ -\ t\^{}\textbackslash{}prime)\ f\^{}\textbackslash{}prime\$}
	\item
	phase coherent update:
	\texttt{\$q\^{}\textbackslash{}prime(t)\ =\ p\^{}\textbackslash{}prime\ +\ (t\ -\ T)\ f\^{}\textbackslash{}prime\$},
	where
	\item
	\texttt{\$q\$}/\texttt{\$q\^{}\textbackslash{}prime\$}: old/new phase
	accumulator
	\item
	\texttt{\$p\$}/\texttt{\$p\^{}\textbackslash{}prime\$}: old/new phase
	offset
	\item
	\texttt{\$f\^{}\textbackslash{}prime\$}: new frequency
	\item
	\texttt{\$t\^{}\textbackslash{}prime\$}: timestamp of setting new
	\texttt{\$p\$},\texttt{\$f\$}
	\item
	\texttt{\$T\$}: ``origin'' timestamp: beginning of experiment, boot of
	device, or arbitrary
	\item
	\texttt{\$t\$}: running time
\end{itemize}

Relative phase updates are called ``continuous phase mode'' and coherent
updates are called ``tracking phase mode'' by some. Phase coherent
updates can be mapped (in software/runtime) to absolute phase updates by
transforming
\texttt{\$p\^{}\textbackslash{}prime\ \textbackslash{}longrightarrow\ p\^{}\textbackslash{}prime\ +\ (t\^{}\textbackslash{}prime\ -\ T)\ f\^{}\textbackslash{}prime\$}.
Since phase coherent updates require large multiplications is is
questionable whether they can and should be implemented in gateware.

It is questionable whether phase coherent updates should or even can be
supported for sweeping \texttt{\$p\$}/\texttt{\$f\$}. They can be
supported for the modulation inputs (see below).

\paragraph{Modulation by RTIO}\label{modulation-by-rtio}

To each spline interpolator (any of the nine \texttt{\$f,p,a,u\$} in the
waveform parametrization) a modulation (summarized as
\texttt{\$e\_\textbackslash{}mathrm\{RTIO\}\$}) by a separate RTIO
channel can be applied.

\begin{itemize}
	\item
	The modulation is an additive offset for frequency and phase
	(\texttt{\$f,p\$}) and a multiplicative offset for amplitudes
	(\texttt{\$u,a\$}).
	\item
	The modulation is times like any other (non-interpolating) RTIO event,
	i.e. \texttt{\$\textbackslash{}leq\ 8\$}ns time resolution and has the
	same value resolution as the spline interpolator it modulates.
	\item
	Default values are 0 for frequency and phase modulation
	(\texttt{\$f,p\$}) and 1 for amplitude modulation (\texttt{\$u,a\$}).
	\item
	Modulation is normalized to full scale.
\end{itemize}

\paragraph{Modulation by local DSP}\label{modulation-by-local-dsp}

In addition to RTIO modulation
\texttt{\$e\_\textbackslash{}mathrm\{RTIO\}\$} there is ``local DSP''
modulation input to each spline interpolator.

\begin{itemize}

	\item
	Same specifications and semantics as the RTIO modulation.
\end{itemize}

\paragraph{Local DSP}\label{local-dsp}

A fully reconfigurable local DSP fabric with multiple IIR filters shall
be included. The DSP switchyard supports servoing applications of
various types.

\begin{itemize}

	\item
	See \href{https://github.com/jordens/redpid}{redpid} for a rough
	feature set.
\end{itemize}

\paragraph{Runtime and kernel
	interface}\label{runtime-and-kernel-interface}

\begin{itemize}
	\item
	Spline knot sequences can be generated off-line and embedded in ARTIQ
	experiments.
	\item
	Spline knot sequences can be generated at compile time.
	\item
	Spline knot sequences can be embedded into ARTIQ experiments and
	emitted to from the core device to the DRTIO channels during the
	experiments.
	\item
	Spline knot sequences can be computed dynamically on core device.
	\item
	Instead of emitting them directly to the DRTIO channel, spline knot
	sequences can be emitted into a named DMA context which stores the
	RTIO events in memory (either on the core device or right at the DRTIO
	channel in the card's DRAM) for later recall.
	\item
	Stored, named DMA segments can be replayed by name.
	\item
	Given enough slack to transmit DRTIO events and fill the channel FIFOs
	(from core device or from any DMA source), all boards, all channels,
	all splines can burst \texttt{\$\textbackslash{}geq128\$} knots each
	at \texttt{\$\textbackslash{}geq125\$}MHz (BRAM FIFO limited). This is
	independent of whether the events are computed dynamically, off-line,
	embedded, reside in core device DRAM or remote DRAM.
	\item
	When sourcing waveforms from core device memory, the sustained
	aggregated spline knot rate across all interpolators is
	\texttt{\$\textbackslash{}geq2\$}MHz.
	\item
	Sourcing from remote DRTIO DMA the spline knot rate per board
	(aggregated over all channels and all interpolators on that board) is
	TBD MHz sustained for TBD knots (DRAM limited).
	\item
	Supports setting \texttt{\$e\_\textbackslash{}mathrm\{DRTIO\}\$} using
	standard DRTIO events.
	\item
	Supports configuring the DAC through RTIO-SPI
	\item
	Utility functions shall be made available to users for processing
	spline waveforms (scaling in value and time, resampling).
	\item
	Given a periodically sampled waveform (vector of values) routines
	shall
	
	\begin{itemize}
		\item
		generate a spline waveform with a fixed knot duration
		\item
		generate a spline waveform with specified knot count and variable
		knot duration
		\item
		generate a spline waveform with minimal knot count and specified RMS
		error
	\end{itemize}
	\item
	given user-supplied spline waveform routines shall
	
	\begin{itemize}
		\item
		generate a periodically sampled waveform (vector of values) with
		user specified resolution
		\item
		determine validity (in-range)
	\end{itemize}
\end{itemize}

\paragraph{Test Cases}\label{test-cases}

ARTIQ Python programs demonstrating the following will be provided.

\begin{enumerate}
	\def\labelenumi{\arabic{enumi}.}
	\item
	Simultaneous generation of two-tone waveforms on 8 DAC channels where
	\texttt{\$f\_\{1\}=f\_\{0\}+\textbackslash{}Delta\$} and
	\texttt{\$f\_\{2\}=f\_\{0\}-\textbackslash{}Delta\$} where
	\texttt{\$f\_\{0\}=200\$}~MHz and
	\texttt{\$\textbackslash{}Delta={[}0,50{]}\$}~MHz.
	\item
	Playing a spline knot sequence demonstrating each spline interpolator
	in turn.
	\item
	Replaying a 128 knot two-tone amplitude sequence from remote DMA.
	\item
	Phase/frequency/amplitude shifting that sequence using
	\texttt{\$e\_\textbackslash{}mathrm\{DRTIO\}\$}.
	\item
	Demonstrate relative and absolute phase mode.
	\item
	Demonstrate deterministic channel alignment to one DAC clock cycle.
	\item
	Demonstrate external and internal clocking.
\end{enumerate}

\subsubsection{Sayma SAWG data rate
	constraints}\label{sayma-sawg-data-rate-constraints}

The fast smart arbitrary waveform channels require a significant amount
of logic resources but also necessitate fulfilling several interacting
constraints on operating frequencies and clock ratios.

For the DAC channel data rate
\texttt{\$f\_\textbackslash{}mathrm\{DATA\}\$} on the JESD204B link, the
following rules need to be observed.

\begin{itemize}
	\item
	\texttt{\$t\_\textbackslash{}mathrm\{DATA\}\ =\ t\_\textbackslash{}mathrm\{RTIO\textbackslash{}\_FINE\}\$}.
	DAC samples need to mesh with RTIO timestamps (e.g.~RF switches on
	TTLs and SYS\_REF tagging), otherwise DAC timing is not
	sample-accurate and samples will beat around RTIO timestamps. The RTIO
	timestamp granularity is a global design variable of an ARTIQ DRTIO
	fabric instance. The granularity does not need to be 1ns and can
	easily be altered globally, but it needs to be the same across the
	entire DRTIO fabric. If e.g.~the core device has a coarse clock of
	125MHz and the high resolution TTL provide three more bits of
	resolution, then the fine timestamp granularity needs to be 1ns (or an
	integer submultiple) everywhere.
	\item
	\texttt{\$t\_\textbackslash{}mathrm\{SLOWDDS\}/k\ =\ t\_\textbackslash{}mathrm\{FASTDDS\}\ =\ t\_\textbackslash{}mathrm\{DATA\}\$}
	with \texttt{\$k\$} a power of two. The accumulator phasing and
	datapath parallelization methods that allow generating multiple
	samples in a single clock cycle only work for powers of two.
	\item
	\texttt{\$t\_\textbackslash{}mathrm\{SLOWDDS\}\$} can potentially be
	as low as 4ns on Kintex 7 with speed grade 2 or better, certainly as
	low as 5ns. The possibility of 4ns fabric timing would need to be
	explored and verified.
	\item
	\texttt{\$t\_\textbackslash{}mathrm\{SLOWDDS\}\ =\ m\ t\_\textbackslash{}mathrm\{RTIO\textbackslash{}\_FINE\}\$}:
	The spline interpolators, RTIO updates, and the slow DDS should mesh
	with the fine timestamp (e.g.~RF switches on TTLs).
	\item
	\texttt{\$t\_\textbackslash{}mathrm\{SLOWDDS\}\ =\ p\ t\_\textbackslash{}mathrm\{RTIO\}\$}:
	The spline interpolators, RTIO updates, and the slow DDS should mesh
	with the coarse timestamp (e.g.~relative to RF switches on coarse
	TTLs). \texttt{\$p\$} is a power of two in the current ARTIQ
	architecture.
	\item
	\texttt{\$f\_\textbackslash{}mathrm\{DATA\}\ \textbackslash{}leq\ 1.09\textbackslash{},\textbackslash{}mathrm\{GHz\}\$}
	or even  1.03,{GHz}\$ for typical DAC and FPGA transciever line rate.
\end{itemize}

The DAC sample rate \texttt{\$f\_\textbackslash{}mathrm\{DAC\}\$} after
interpolation and up-sampling from
\texttt{\$f\_\textbackslash{}mathrm\{DATA\}\$} needs to satisfy:

\begin{itemize}
	\item
	\texttt{\$f\_\textbackslash{}mathrm\{DATA\}\ \textbackslash{}leq\ 2.4\textbackslash{},\textbackslash{}mathrm\{GHz\}\$}:
	Typical DAC sample rate
	\item
	\texttt{\$f\_\textbackslash{}mathrm\{DAC\}\ =\ q\ f\_\textbackslash{}mathrm\{DATA\}\$}
	with
	\texttt{\$q\ \textbackslash{}in\ \textbackslash{}\{1,\ 2,\ 4,\ 8\textbackslash{}\}\$}:
	Available interpolation options
\end{itemize}

\paragraph{Logic and RAM}\label{logic-and-ram}

\begin{itemize}
	\item
	ARTIQ device CPU(s) and miscellaneous logic resources provide a good
	estimate for the additional logic required to support DRTIO. The
	kc705-nist\_qc2 design occupies 23k LUT and 5Mb BRAM. The
	pipistrello-nist\_qc1 design uses 15k LUT and 1Mb BRAM (on a slightly
	different architecture).
	\item
	parallelized FIR: 4 channel, 4x parallelism, 30 taps: 240 DSP
	\item
	parallelized HBF + tricks: 4 channel, 4x parallelism, 30 taps: 120 DSP
	\item
	RTIO FIFOs: 4 channel, 128 knots per RTIO channel: 4Mb
	\item
	PID, extrapolating from redpid (xc7z010): 2 channel 125MHz ADC/DAC +
	misc DSP, full servo crossbar matrix: 13 kLUT, 50 DSP
\end{itemize}

Several design studies were performed for different configurations of
the Sayma SAWG channels:

\begin{itemize}
	\item
	Sayma initial SAWG on kc705: 2 channel, 8x parallelism, 125MHz: 28k
	LUT
	\item
	Sayma advanced draft SAWG on kc705: 4 channel, 4x parallelism, 200MHz:
	33k LUT
	\item
	Sayma advanced draft SAWG on kc705: 4 channel, 8x parallelism, 125MHz:
	53k LUT
	\item
	Sayma advanced draft SAWG on kc705: 8 channel, 8x parallelism, 125MHz:
	106k LUT
	\item
	Sayma advanced draft SAWG on kcu105: 4 channel 4x parallelism, 200MHz:
	33k LUT
\end{itemize}

\paragraph{Data and sample rates}\label{data-and-sample-rates}

\textbf{Somewhere in the Sayma docs, we should have a page about clock
	distribution, giving users an overview of the different constrains that
	exist for clocking. This section should be merged into that and/or the
	SAWG docs.} The following choices for data rates and lanes appear to be
interesting (BW: bandwidth; SSB: single sideband; DSB: dual sideband;
``size'': resource usage in units of 13k LUTs per channel):

\begin{longtable}[]{@{}lllllll@{}}

	\begin{minipage}[b]{0.14\columnwidth}\raggedright\strut
		\texttt{\$f\_\textbackslash{}mathrm\{DAC\}\$}\strut
	\end{minipage} & \begin{minipage}[b]{0.15\columnwidth}\raggedright\strut
	\texttt{\$f\_\textbackslash{}mathrm\{DATA\}\$}\strut
\end{minipage} & \begin{minipage}[b]{0.09\columnwidth}\raggedright\strut
line rate\strut
\end{minipage} & \begin{minipage}[b]{0.06\columnwidth}\raggedright\strut
lanes\strut
\end{minipage} & \begin{minipage}[b]{0.07\columnwidth}\raggedright\strut
``size''\strut
\end{minipage} & \begin{minipage}[b]{0.14\columnwidth}\raggedright\strut
\texttt{\$f\_1,f\_2\$} DSB BW\strut
\end{minipage} & \begin{minipage}[b]{0.14\columnwidth}\raggedright\strut
BW mix 2nd+3rd\strut
\end{minipage}\tabularnewline

\endhead
\begin{minipage}[t]{0.14\columnwidth}\raggedright\strut
	2.4GHz\strut
\end{minipage} & \begin{minipage}[t]{0.15\columnwidth}\raggedright\strut
600MHz\strut
\end{minipage} & \begin{minipage}[t]{0.09\columnwidth}\raggedright\strut
6GHz\strut
\end{minipage} & \begin{minipage}[t]{0.06\columnwidth}\raggedright\strut
8\strut
\end{minipage} & \begin{minipage}[t]{0.07\columnwidth}\raggedright\strut
4\strut
\end{minipage} & \begin{minipage}[t]{0.14\columnwidth}\raggedright\strut
150MHz\strut
\end{minipage} & \begin{minipage}[t]{0.14\columnwidth}\raggedright\strut
300--600--900MHz\strut
\end{minipage}\tabularnewline
\begin{minipage}[t]{0.14\columnwidth}\raggedright\strut
	2GHz\strut
\end{minipage} & \begin{minipage}[t]{0.15\columnwidth}\raggedright\strut
1000MHz\strut
\end{minipage} & \begin{minipage}[t]{0.09\columnwidth}\raggedright\strut
10GHz\strut
\end{minipage} & \begin{minipage}[t]{0.06\columnwidth}\raggedright\strut
8\strut
\end{minipage} & \begin{minipage}[t]{0.07\columnwidth}\raggedright\strut
8\strut
\end{minipage} & \begin{minipage}[t]{0.14\columnwidth}\raggedright\strut
125MHz\strut
\end{minipage} & \begin{minipage}[t]{0.14\columnwidth}\raggedright\strut
500--1000--1500MHz\strut
\end{minipage}\tabularnewline
\begin{minipage}[t]{0.14\columnwidth}\raggedright\strut
	1.6GHz\strut
\end{minipage} & \begin{minipage}[t]{0.15\columnwidth}\raggedright\strut
800MHz\strut
\end{minipage} & \begin{minipage}[t]{0.09\columnwidth}\raggedright\strut
8GHz\strut
\end{minipage} & \begin{minipage}[t]{0.06\columnwidth}\raggedright\strut
8\strut
\end{minipage} & \begin{minipage}[t]{0.07\columnwidth}\raggedright\strut
4\strut
\end{minipage} & \begin{minipage}[t]{0.14\columnwidth}\raggedright\strut
200MHz\strut
\end{minipage} & \begin{minipage}[t]{0.14\columnwidth}\raggedright\strut
400--800--1200MHz\strut
\end{minipage}\tabularnewline
\begin{minipage}[t]{0.14\columnwidth}\raggedright\strut
	300MHz\strut
\end{minipage} & \begin{minipage}[t]{0.15\columnwidth}\raggedright\strut
300MHz\strut
\end{minipage} & \begin{minipage}[t]{0.09\columnwidth}\raggedright\strut
6GHz\strut
\end{minipage} & \begin{minipage}[t]{0.06\columnwidth}\raggedright\strut
4\strut
\end{minipage} & \begin{minipage}[t]{0.07\columnwidth}\raggedright\strut
2\strut
\end{minipage} & \begin{minipage}[t]{0.14\columnwidth}\raggedright\strut
150MHz\strut
\end{minipage} & \begin{minipage}[t]{0.14\columnwidth}\raggedright\strut
150--300--450MHz\strut
\end{minipage}\tabularnewline

\end{longtable}

For 4 JESD lanes, use DAC ``mix mode'' (switching up-conversion by
\texttt{\$f\_\textbackslash{}mathrm\{DAC\}\$}) to emphasize second
Nyquist zone from \texttt{\$f\_\textbackslash{}mathrm\{DAC\}/2\$} to
\texttt{\$f\_\textbackslash{}mathrm\{DAC\}\$}. Zeros at 0Hz and
\texttt{\$2\textbackslash{}times\ f\_\textbackslash{}mathrm\{DAC\}\$}.

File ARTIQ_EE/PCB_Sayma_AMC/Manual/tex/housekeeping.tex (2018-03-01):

\section{Housekeeping Signals}
Both MMC and FPGA can acces to any of I2C buses as is in Figure \ref{I2C}. MMC collects all data from all sensors connected to I2C bus. Then the data can be transfered via IPMI to MCH. For now MCH get only information about AMC and RTM to allow power supply.

\subsection{sensors}
Temperature:\\
%\begin{itemize}
%	\item IC8 (0x4B) -NOR Flash
%	\item IC34 (0x49) -FPGA
%	\item IC35 (0x4A)-under SFPs
%	\item IC36 (0x4F)-power section
%	\item IC37 (0x24) -middle od the board
%\end{itemize}
\begin{longtable}{|c|c|c|c|c|}\hline
	No & Addr. & placement & Type & Accuracy \\ \hline
	IC8 & 0x4B & NOR Flash & LM75 & +/- 2 \\ \hline
	IC34 & 0x49 & FPGA & LM75 & +/- 2  \\ \hline
	IC35 & 0x4A & Under SFPs & LM75 & +/- 2  \\ \hline	
	IC36 & 0x4F & power section & LM75 & +/- 2  \\ \hline
	IC37 & 0x24 & middle of the board & MAX664A & +/- 1 \\ \hline
\end{longtable}

All temperature sensors are tied tohether to one I2C bus - SENS\_I2C. \\

Current:
%\begin{itemize}
%	\item IC27 (0x40)-RTM\_P12V0
%	\item IC28 (0x41)-FMC\_P12V0
%\end{itemize}
\begin{longtable}{|c|c|c|c|c|}\hline
		No & Addr. & placement & Type & Accuracy \\ \hline
		IC27 & 0x40 &RTM\_P12V0& INA219 & +/- 0.2\% \\ \hline
		IC28 & 0x41 &FMC\_P12V0& INA219 & +/- 0.2\% \\ \hline
\end{longtable}

All current sensors are tied tohether to one I2C bus - PM\_I2C. \\

\subsection{Safety interlocks}

Temperature interlock is available on RTM board only and gets activated after reaching 80 degrees. This is hardware interlock and cannot be deactivated. Dedicated LED (LD15) gets on and RTM power supply is off until the temperature is exceeded

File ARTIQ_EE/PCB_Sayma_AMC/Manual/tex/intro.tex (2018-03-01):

%\section{Introduction to Micro TCA}

%The MTCA platform is available on the market for over
%ten years. It evolved from telecommunication ATCA standard. The MTCA sandard utilizes ATCA-defined AMC boards
%used directly in dedicated chassis. It also defines MTCA
%Carrier Hub (MCH) which controlls multiple slave boards, known as Advanced Mezzanine Cards (AMCs) via a high-speed digital backplane. AMC card can be equipped with FPGA Mzzanine Cards (FMCs) which are I/O modules pluggable to High-pin Count (HPC) or Low-pin Count (LPC) connector. 
%
%%which consists of Ethernet hub and crate
%%management system. 
%The MTCA crates are available in several
%form-factors for industrial, aviation and military use.
%User can easily extend and adopt the standard to particular application by selection of
%proper chassis, cooling method, computing and connectivity
%technology while keeping same mechanical, electrical standard and software architecture.\\

%MicroTCA (uTCA) is Sinara's preferred form-factor for hardware with high-speed data converters requiring deterministic phase control, such as the Sayma 2.4GSPS smart arbitrary waveform generator (SAWG).
%
%uTCA is a modular, open standard originally developed by the telecommunications industry. It allows a single rack master -- the Micro TCA Carrier Hub (MCH) -- to control multiple slave boards, known as Advanced Mezzanine Cards (AMCs) via a high-speed digital backplane. uTCA chassis and backplanes are available commercially of the shelf (COTS).
%%
%We make use of the most recent extension to the uTCA standard, uTCA.4. Originating in the high-energy and particle physics (HEPP) community, uTCA.4 introduces rear-transition modules (RTMs) along with a second backplane for low-noise RF signals (RFBP). Each RTM connects to an AMC (one RTM per AMC). Typically, the AMCs hold FPGAs and other high-speed digital hardware, communicating with the MCH via gigabit serial links over the AMC backplane. The RTMs hold data converters and other low-noise analog components, controlled by the corresponding AMC. The RFBP provides low-noise clocks and local oscillators (LOs). The RTMs and RFBP are screened from the AMCs to minimise interference from the high-speed digital logic

\section{Glossary}

\begin{description}
	\item[AMC Module or Modul] An AMC Module is a mezzanine or modular add-on card that extends the
	functionality of a Carrier Board. The term is also used to generically refer to the
	different varieties of Multi-Width and Multi-Height Modules.
	\item[Fat Pipes] Ports 4 though 11 of the AMC Connector constitute the Fat Pipes Region. This
	Region of Ports is intended for the assignment of multiple Lane interfaces, also
	called “fat pipes”. Fat Pipe 1 [Ports 4-7], Fat Pipe [Ports 8-11].
	\item[FMC] FPGA Mezzanine Card
	\item[Hot Swap] To remove a component (e.g., an AMC Module) from a system (e.g., an AMC Carrier
	AdvancedTCA Board) and plug in a new one while the power is still on and the
	system is still operating.
	\item[Management Power or MP] The 3.3V power for a Module's Management function, individually provided to each Slot by the Carrier
	\item[IPMB] ntelligent Platform Management Bus. The lowest level hardware management bus
	as described in the Intelligent Platform Management Bus Communications Protocol
	Specification.
	\item[MGT] Multi-Gigabit Transceiver
	\item[MMC] Module Management Controller. The MMC is the required intelligent controller that
	manages the Module and is interfaced to the Carrier via IPMB-Local
	\item[RTM] Rear Transition Module
\end{description}

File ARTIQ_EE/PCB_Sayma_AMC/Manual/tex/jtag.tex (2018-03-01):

\section{JTAG}
Scansta112 is 7-Port Multidrop JTAG Multiplexer. It is used to partition scan chains into managable sizes, or to isolate specific devices onto a separate chain. By default Scansta input signal is from IDC header. AMC JTAG is connected to Master Port on SCANSTA, so it can be used as Master or Slave module. The rest modules (MMC, FPGA, FMC, RTM) are tied to slave SCANSTA outputs. \\

Tere are two JTAG sources – either AMC connector ( JSM module) or USB to JTAG bridge (FTDI chip). There is also onboard JTAG connector (Xilinx type) -J3. Insertion of JTAG programmer probe deactivates the FTDI JTAG connectivity and forces SCANSTA chip set this port as master port. By default SCANSTA selects AMC port as master one.\\

In Sayma AMC, SCANSTA112 is used in Transparent Sticher Mode. In this mode, the IC can be configured via hardware to skip the addressing protocol needed, sothere is no need to run a SVF configuration file on IMPACT when programming the FPGA bitstream.\\
	\begin{figure}[htbp!]
		\centering
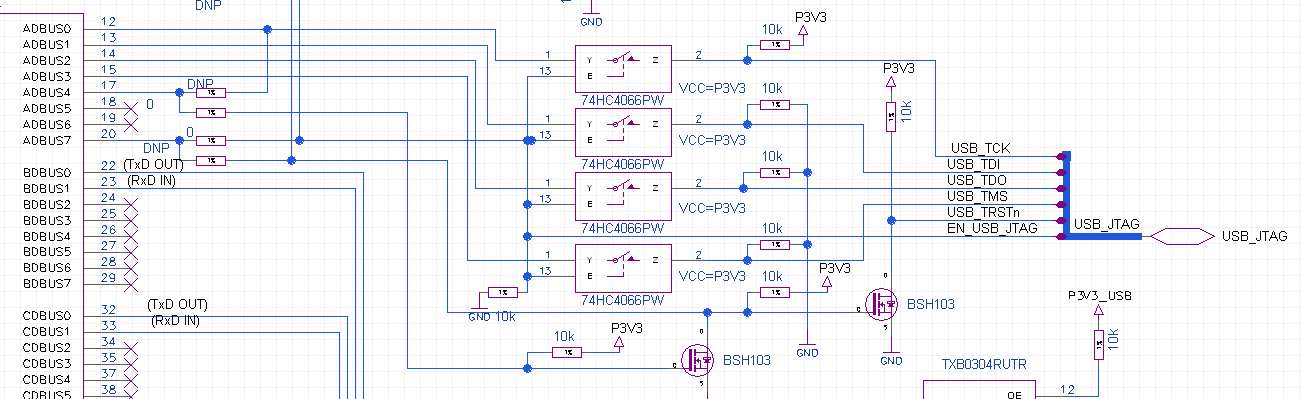
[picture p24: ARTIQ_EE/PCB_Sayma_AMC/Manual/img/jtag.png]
		\\
		\caption{USB-->JTAG} 
	\end{figure}
\clearpage	
General block scheme of Scansta connections is shown below.\\
	
		\begin{figure}[htbp!]
			\centering
			\\
			\caption{SCANSTA bloch scheme} 
		\end{figure}
		
	\textit{\textbf{Note:} The FMC2 and PS is not used.}\\

Each of JTAG slave devices is connected directly to SCANSTA. SCANSTA allows to connect all devices in chain witn an option to pass one or more devices, intention in Figure \ref{jtagchain}.

		\begin{figure}[htbp!]
			\centering
			\\
			\caption{SCANSTA JTAG chain} \label{jtagchain}
		\end{figure}

Simplified instruction if using SCANSTA can be found under: \href{http://www.ti.com/lit/an/snla068c/snla068c.pdf}{http://www.ti.com/lit/an/snla068c/snla068c.pdf}

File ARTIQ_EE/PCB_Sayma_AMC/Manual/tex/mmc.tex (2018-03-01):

\section{MMC}

\subsection{MMC steps during booting}

\begin{itemize}

\item configures CPU, UART from own FLASH 
\item sets IO port directions
\item enables VCCINT PSU
\item enables P5V0 PSU (helper PSU)
\item enables Exar PSU. It boots from its own EEPROM
\item waits 200ms
\item configures SCANSTA chip in stitcher mode. If RTM is inserted, it enables its JTAG port
\item configures I2C switch base address for master ports - MMC, FPGA
\item initializes default RTM power state to off
\item initializes Ethernet PHY chip in RGMII mode using pin strap.
\item waits 200ms
\item initializes I2C controller and chain (switch)
\item configures Si5324
\item checks if RTM is inserted, if yes, then enables its power, waits 200ms and initializes RTM power supply via RTM\_I2C. It also configures Si5324 on RTM
\item runs task.\\
 
The task performs following functions:

\item checks if FPGA is configured. If not, it keeps Ethernet PHY in reset state. Once FPGA gets configured, it initializes the PHY.
\item checks if RTM is unplugged. If not, it switches the power off to make sure it is off during hotplug.
\end{itemize}
\textit{\textbf{Note:}Configuration CPU, UART does not affect with any changes of LED indicators.}

\subsection{Bootstraping}
To compile binaries \href{https://www.nxp.com/products/processors-and-microcontrollers/arm-based-processors-and-mcus/lpc-cortex-m-mcus/lpc1100-cortex-m0-plus-m0/lpcxpresso-ide-v8.2.2:LPCXPRESSO?tab=Design_Tools_Tab}{LPCXpresso} in newest version is needed.\\
\href{https://www.nxp.com/docs/en/user-guide/LPCXpresso_IDE_User_Guide.pdf}{LPCXpresso User Guide}

Another option is to compile under Linux using cmake toolchain in version 4.9.3.
\begin{lstlisting}
cmake & arm-none-eabi-gcc
\end{lstlisting}

\begin{itemize}
	\item Header flashing

The MMC can be upgraded by USB cable and NXP programmer(can be used other programmer but make sure that header shorts pins 3, 5, 9) using  \href{http://www.flashmagictool.com/}{Flashmagic} or any other software which can talk with NXP bootloader. The tested programmer is LPCLink V2. Flashing using programmer allows to debug.

	\item USB flashing
The MMC can be upgraded using USB and flashmagic software. This option only allows to flash IC, without any debug option.
Steps to flash using USB:
\begin{itemize}
	\item Set serial console 115200 8n1
	\item Press front-panel button -PB3 to trigger MMD to dump to serial console
	\item Set LPC1776, 8MHz oscillator, select hex file and press start
\end{itemize}

\end{itemize}

The source code is written in C and can be found on github.\\ 
\textbf{Source code:} \href{https://github.com/m-labs/sinara/tree/master/SAYMA\_firmware}{https://github.com/m-labs/sinara/tree/master/SAYMA\_firmware}.\\
\textbf{pre-compiled binary:} \href{https://github.com/m-labs/mmc-firmware/releases}{https://github.com/m-labs/mmc-firmware/releases}\\

%\subsection{Functionality}
%
%\todo[inline]{needed?}

\subsection{Exar debugging}
 
In case of chip failure, i.g.overvoltage, overcurrent, etc., there is possibility  to check chip status via UART. In this case in UART console, Exar register readout can be done by typing 'P' character.\\

	\begin{figure}[htbp!]
		\centering
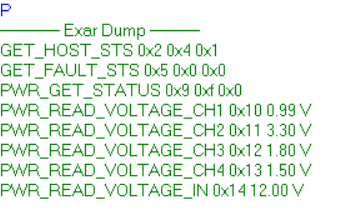
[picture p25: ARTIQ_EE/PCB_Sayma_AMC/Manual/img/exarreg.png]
		\\
		\caption{Exar register } 
	\end{figure}	
\clearpage
\subsection{PHY debugging}

In case of chip failure, there is possibility to check chip status via UART. In this case in UART console, Ethernet PHY content can be read by typing 'E' character

	\begin{figure}[htbp!]
		\centering
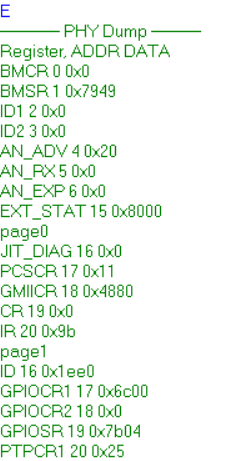
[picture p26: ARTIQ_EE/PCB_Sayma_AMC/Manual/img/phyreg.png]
		\\
		\caption{Ethernet PHY register } 
	\end{figure}

\subsection{Ethernet }

There is no Ethernet sharing between MMC and FPGA due to speed difference between RGMII and RMII. PHY does not provide link speed translation.

\subsection{OpenMMC}

\textbf{OpenMMC Project:}\href{https://github.com/lnls-dig/openMMC}{https://github.com/lnls-dig/openMMC}

\todo[inline]{TBD}

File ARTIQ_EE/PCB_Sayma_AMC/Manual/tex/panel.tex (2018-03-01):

\section{Front panel and headers}

		\begin{figure}[htbp!]
			\centering
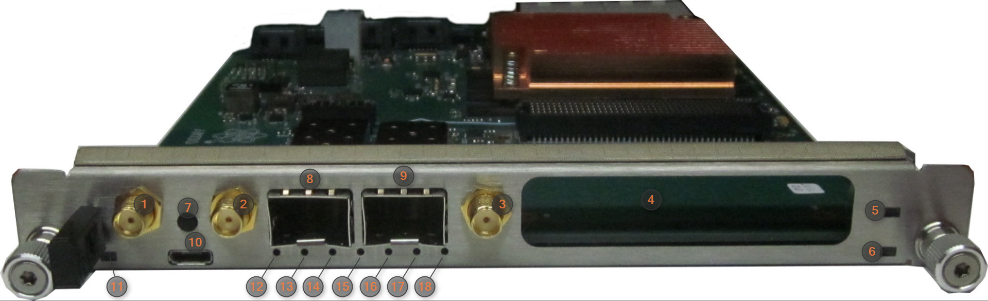
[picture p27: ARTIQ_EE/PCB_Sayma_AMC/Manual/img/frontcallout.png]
			\\
			\caption{Front view}
		\end{figure}
		
		\begin{figure}[htbp!]
			\centering
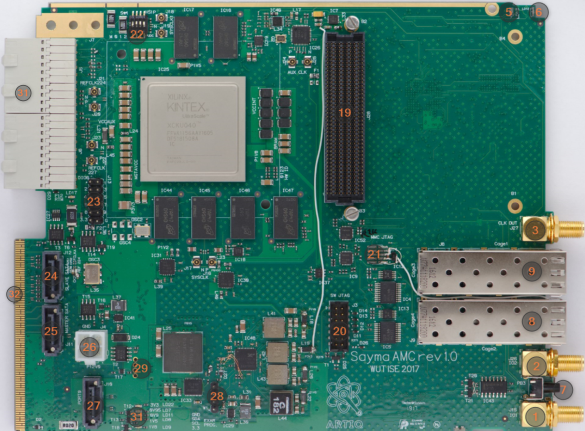
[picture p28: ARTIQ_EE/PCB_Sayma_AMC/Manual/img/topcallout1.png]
			\\
			\caption{Front view}
		\end{figure}

\begin{longtable}{|c|c|c|} \hline
	\multicolumn{3}{|c|}{Call out table } \\ \hline	
	Call out & Designator & Description \\ \hline
	1 & J15 & GPIO - IO1 \\ \hline
	2 & J26 & GPIO - IO2 \\ \hline
	3 & J27 & CLK OUT output driven by Si5324 (CDR\_CLK\_CLEAN3) \\ \hline
	4 & J28 & FMC connector \\ \hline
%	5 & LD13 & Error\\ \hline
%	6 & LD18 & Hot swap \\ \hline
	7 & PB3 & routed to MMC, allows to flash MMC via USB \\ \hline
	8 & cage2 & SFP Cage \\ \hline
	9 & cage1 & SFP Cage \\ \hline
	10 & J1 & Micro USB -->Serial \\ \hline
%	11& LD14 & operation successful  \\ \hline
%	12 & LD16 & SFP LED2 \\ \hline
%	13 & LD3 & SFP LED1 \\ \hline
%	14 & LD6 & LINK UP \\ \hline
%	15 & LD4 & MII MODE \\ \hline
%	16 & LD15 & SFP LED2  \\ \hline
%	17 & LD2 & SFP LED1 \\ \hline
%	18 & LD5 & FPGA ETH \\ \hline
	19 & J28 & FMC header \\ \hline
	20 & J3 & JTAG header connected to SCANSTA\\ \hline
	21 & J14 & MMC JTAG \\ \hline
	22 & SW1 & FPGA MODE, see SW1 paragraph \\ \hline
	23 & J13 & Digital IOs connected to FPGA \\ \hline
	24 & J12 & SLAVE SATA \\ \hline
	25 & J11 & MASTER SATA \\ \hline
	26 & J4 & Power In \\ \hline
	27 & J10 & SATA connected to Port 0 \\ \hline
	28 & W1 & EXAR I2C header \\ \hline
	29 & -- & P12V0 \\ \hline
	30 & -- &  Test points \\ \hline
	31 & J6 & RTM Connector \\ \hline
	32 & J2 & AMC Connector \\ \hline
\end{longtable}

\clearpage
\begin{figure}[htbp!]
	\centering
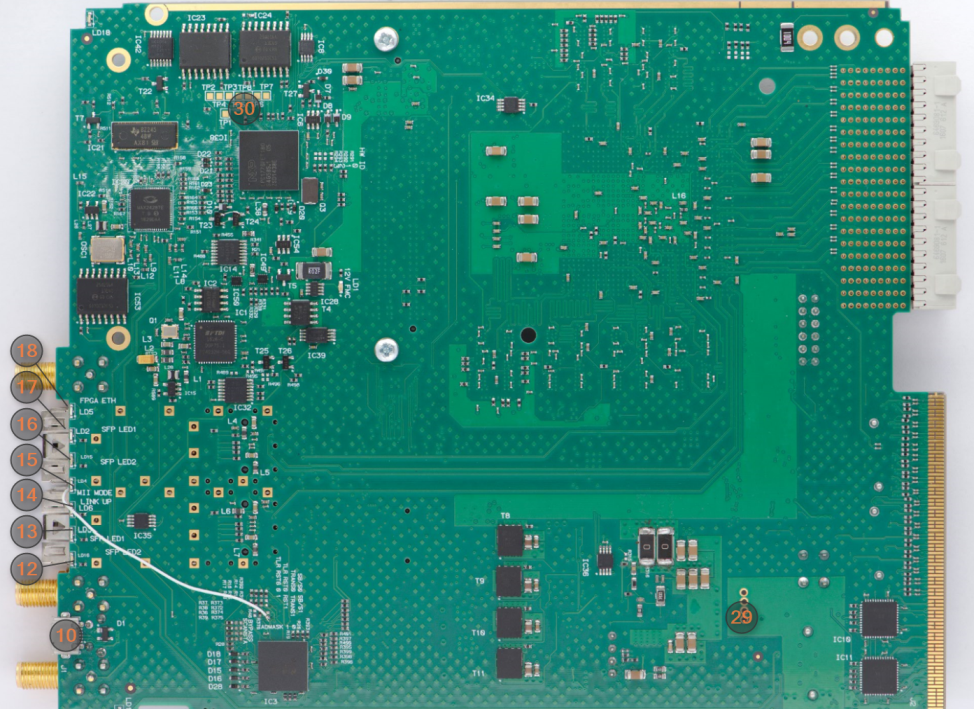
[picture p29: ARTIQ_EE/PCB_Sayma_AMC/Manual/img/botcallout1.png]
	\\
	\caption{Front view}
\end{figure}

Callout 5: LD13 is
\begin{itemize}
	\item off if MMC is ok 
	\item red if MMC is in an error state
\end{itemize}

Callout 6: LD4 is
\begin{itemize}
	\item off the board has initialized in crate
	\item blue if power is cut off and is possible to remove the board.
\end{itemize}

Callout 33: LD21 is
\begin{itemize}
	\item green if FPGA is configured
	\item off if FPGA is not configured
\end{itemize}

Callout 11: LD14 is
\begin{itemize}
	\item green if MMC successfulled operation
	\item off if MMC unsuccessfuled operation
\end{itemize}

Callout 14: LD20 is
\begin{itemize}
	\item green if Link is up
	\item off if Link is down
\end{itemize}
Callout 15: LD18 is
\begin{itemize}
	\item green if Ethernet is in MII mode (mTCA doesn't support 100mbit Ethernet)
	\item off if Ethernet is in RGMII mode
\end{itemize}
%-----------------------------SFP
Callout 12: LD3 is
\begin{itemize}
	\item red if SFP2 - user defined
	\item off if SFP2 - user defined
\end{itemize}
Callout 13: LD6 is
\begin{itemize}
	\item green if SFP2 - user defined
	\item off if SFP2 - user defined
\end{itemize}
Callout 16: LD2 is
\begin{itemize}
	\item red if SFP1 - user defined
	\item off if SFP1 - user defined
\end{itemize}

Callout 17: LD5 is
\begin{itemize}
	\item green if SFP1 - user defined
	\item off if SFP1 - user defined
\end{itemize}

Callout 18: LD19 is
\begin{itemize}
	\item green if - user defined
	\item off if - user defined
\end{itemize}

\begin{longtable}{|c|c|c|c|c|c|c|} \hline
		\multicolumn{7}{|c|}{Power LED table }\\ \hline
	Call out & Designator & Description&  Colour &nominal state& IC &Failure\\ \hline
%	5 & LD13 & Error &Red & off &MMC & on \\ \hline
%	6 & LD4 & Hot Swap & Blue & on&  MMC &  off\\ \hline
%	6 & LD21 & FPGA config done & Green & on& FPGA &off \\ \hline 
%	11 & LD14 & Operation succesful& Green & on& MMC &off\\ \hline
%	12 & LD3 & SFP2 LED2 & Red &on& FPGA & off\\ \hline
%	13 & LD6 & SFP2 LED1 & Green &on & FPGA&off \\ \hline
%	14 & LD20 & LINK UP &  Green &on & MAX24287&off \\ \hline
%	15 & LD18 & MII MODE & Green & on& MMC&off \\ \hline
%	16 & LD2 & SFP1 LED2 & Red & on& FPGA &off\\ \hline
%	17& LD5 & SFP1 LED1 & Green &on & FPGA& off\\ \hline
%	18 & LD19 & FPGA ETH & Green &on & MMC &off\\ \hline
	30 & LD22 & 3V3 & Green & on & Power & off \\ \hline
	30 & LD7 & 0V95 & Green & on & Power & off \\ \hline 
	30 & LD11 & 0V9 & Green & on & Power & off \\ \hline 
	30 & LD8 & 1V5 & Green & on & Power & off \\ \hline 
	30 & LD9 & 1V8 & Green & on & Power & off \\ \hline 
	30 & LD10 & 12V & Green & on & Power & off \\ \hline  
\end{longtable}

\subsection{Headers pinout}

		\begin{figure}[htbp!]
			\centering
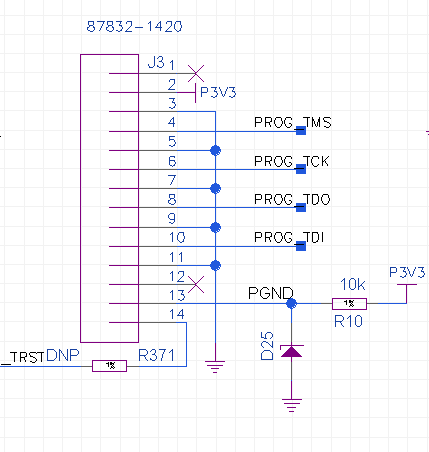
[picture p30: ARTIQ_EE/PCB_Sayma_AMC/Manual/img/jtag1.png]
			\\
			\caption{JTAG - Call out 20}
		\end{figure}

		\begin{figure}[htbp!]
			\centering
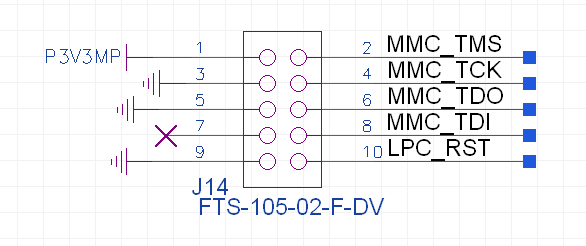
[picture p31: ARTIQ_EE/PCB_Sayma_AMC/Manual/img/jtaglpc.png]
			\\
			\caption{JTAG - Call out  21}
		\end{figure}
		
		\begin{figure}[htbp!]
			\centering
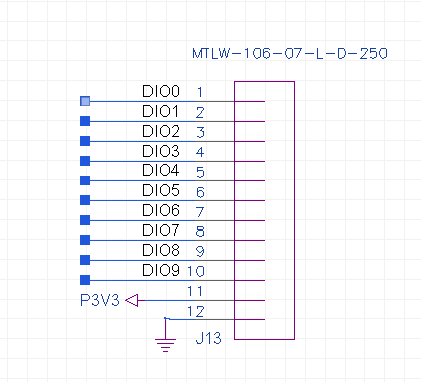
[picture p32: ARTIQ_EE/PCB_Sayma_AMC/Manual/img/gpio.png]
			\\
			\caption{DIO - Call out 23}
		\end{figure}

\clearpage

\begin{longtable}{|c|c|c|} \hline
		\multicolumn{3}{|c|}{Tespoints table - Call out 30}\\ \hline
	TPx & Sig Name & LPC pin \\ \hline
	TP1 & MII1\_col & C13 \\ \hline
	TP2 & SDCLK & J10 \\ \hline
	TP3 & SDCMD & K14 \\ \hline
	TP4 & SDPWR & K11 \\ \hline
	TP5 & SDDAT0 & L14 \\ \hline
	TP6 & SDDAT1 & M12 \\ \hline
	TP7 & SDDAT2 & N14 \\ \hline
	TP8 & SDDAT3 & M11 \\ \hline
	
\end{longtable}	

\subsection{Location ICs}

		\begin{figure}[htbp!]
			\centering
			\\
			\caption{Top}
		\end{figure}
		\begin{figure}[htbp!]
			\centering
			\\
			\caption{Bot}
		\end{figure}
\clearpage

\begin{longtable}{|c|c|c|} \hline
		\multicolumn{3}{|c|}{ICs Location}\\ \hline	
	Ux & IC & Description \\ \hline
	U1 & Kintex& FPGA \\ \hline
	U2 & LTC 6957&Low Phase Noise Buffer \\ \hline
	U4 & TPS53353  & P0V9\\ \hline
	U5 & XR77129 & EXAR\\ \hline
	U6 & TPS 74401  & P1V2\\ \hline
	U7 &  TPS 74401 & P0V95 \\ \hline
	U3 & SI5324C& Clock recovery \\ \hline
	U8 & TCA9548 &I2C switch - MMC\\ \hline
	U9 & TCA9548 &I2C switch - FPGA\\ \hline
	U10 & 74HC4066PW & Analog switch - Flash update\\ \hline
	U11 & N25Q256A13ESF40 & NOR Flash\\ \hline
	U12 & N25Q256A13ESF40 & NOR Flash\\ \hline
	U13 & SN74CB3Q32245ZKE  & Digital Bus switch - RGMI/MII\\ \hline
	U14 & LPC1776FET180  & MMC\\ \hline
	U15 & MAX24287ETK+ &ETH switch\\ \hline
	U16 & AN74CBT3257PW  & USB console switch\\ \hline
	U17 & N25Q256A13ESF40 & NOR Flash - MMC\\ \hline
	U18 & M93C46  & EEPROM\\ \hline
	U19 & F4232H-56Q & USB-UART Bridge \\ \hline
	U20 & 74HC4066PW & USB-UART Switch\\ \hline
	U21 & SCANSTA112SM & SCANSTA JTAG Switch\\ \hline
	U22 & FDMS7608S &EXAR Transistors \\ \hline
	U23 & SN65MLVD040RGZT &LVDS transceiver\\ \hline
	U24 & SN65MLVD040RGZT &LVDS transceiver \\ \hline
	U25 & TPS62175  & P5V0 \\ \hline
	U26 & TPS62175 & P3V3 \\ \hline
\end{longtable}

\subsection{SW1}

SW1 is used to chose configuration mode of the FPGA. Configuration modes define the specifics of how the FPGA will interact with the data source, external control logic. SW1 is tied directly to Bank 0 pf FPGA. All pins have pull up, switching SW1 proceed of connecting to lower potential.
\begin{longtable}{|c|c|c|c|} \hline
			\multicolumn{4}{|c|}{SW1 table}\\ \hline
	M0 & M1 & M2 & Description \\ \hline
	0 & 0 & 0 & Master Serial Mode \\ \hline
	0 & 0 & 1 & Master Parallel Up \\ \hline
	0 & 1 & 1 & Master Parallel Down \\ \hline
	1 & 0 & 1 & Peripheral mode \\ \hline
	1 & 1 & 1 & Slave Serial mode \\ \hline
	
\end{longtable}

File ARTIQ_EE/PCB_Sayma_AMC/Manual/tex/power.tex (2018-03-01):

\section{Power}
\subsection{Power supply}
The card can operate as stand alone devide, or plugged into a uTCA crate. While working standalone the power is provided by Molex Connector(39-28-1043) -J4. The pinout is shown in Figure  \ref{power}.\\
When the card is inserted to the crate the power is applied from AMC connector -J2, +12V (8 power lines) and +3.3\_MP(1 line).
At the begening +3.3\_MP power up the MMC, then +12 is converted to lower voltages, simplified power map is in figure \ref{powermap}. All on board voltages (exept P3V3\_MP) are enabled by MMC. There are two types of power distributors, fixed LDOs and Exar chip - quad channel digital Pulse Width Modulated (PWM) step down (buck) controller. Exar allows for adjust power parameters and for set particular power oorder. Exar firmware monitors current and responds if its too high.  Additionaly all LDOs have connected PowerGood outputs so it is possible to read the proper state of all power busses. 
\todo[inline]{TBD Can MMC readout Exar debug information?}
\todo[inline]{TBD voltage noise}

	\begin{figure}[htbp!]
		\centering
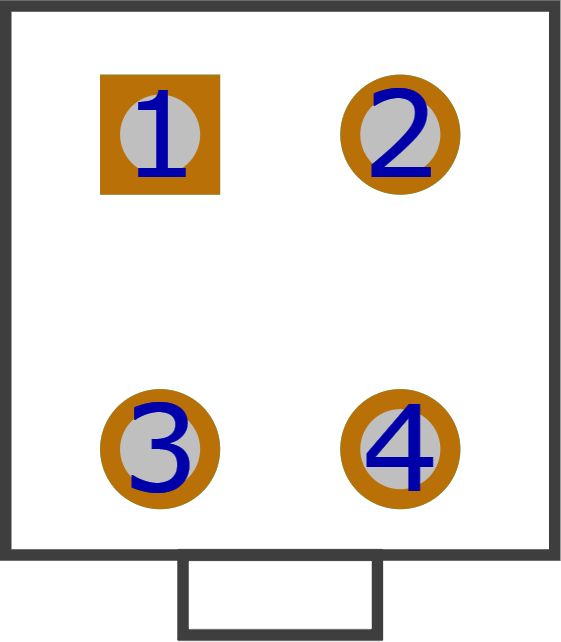
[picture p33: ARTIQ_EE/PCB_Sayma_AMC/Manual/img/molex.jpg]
		\\
		\caption{Power connector} \label{power}
	\end{figure}
\begin{center}
\begin{tabular}{|c|c|} \hline
	{\LARGE GND} & {\LARGE GND} \\ \hline
	{\LARGE +12} & {\LARGE +12} \\ \hline
\end{tabular}
\end{center}

Maximum board(AMC+RTM module) power consumption estimate to 3A @ 12V.\\

	\textit{\textbf{Note:} Please note that power consumption mostly depends from FPGA configuration. \\}

\begin{itemize}

\item Input voltage range: 10.8-13.2 [V]\\
\item The board needs active cooling. Approx. 20CFM in 20 C air.\\

\end{itemize}

Exar chips are configured via PM\_I2C bus (I2CMUX5) or directly by connecting to W1 (call-out 28) header. For proper configuration \textbf{Exar Power Architect} in version \textbf{5.2-r1} is needed.
% Configuration files can be found at github in folder \href{https://github.com/m-labs/sinara/tree/master/EXAR\_config}{m-labs/sinara/Exar\_config}\\

\noindent
\textbf{Exar Power Archtect 5.2-r1:}
\href{https://www.exar.com/content/document.ashx?id=21632}{https://www.exar.com/content/document.ashx?id=21632}\\
\textbf{Configuration files:}
\href{https://github.com/m-labs/sinara/tree/master/EXAR\_config}{https://github.com/m-labs/sinara/tree/master/EXAR\_config}\\
\textbf{Datasheet:}\href{https://www.exar.com/ds/xr77129_1a_120514.pdf}{https://www.exar.com/ds/xr77129\_1a\_120514.pdf}\\
\textbf{Quick Start Guide:} \href{https://www.exar.com/files/powerxr/PA5-QSG_110_010614.pdf}{https://www.exar.com/files/powerxr/PA5-QSG\_110\_010614.pdf}\\

Actual voltages and current consumption, temperature can be found in Chip Dashboard. There is also oportunity to adjust settings.

\begin{figure}[htbp!]
	\centering
	\\
	\caption{Chip Dashboard} 
\end{figure}

\subsection{Power configuration} 

\subsubsection{Power map}

	\begin{figure}[htbp!]
		\centering
		\\
		\caption{Power map} \label{powermap}
	\end{figure}
\clearpage	

\begin{longtable}{|c|c|c|} \hline
\multicolumn{3}{|c|}{voltages and currents}	\\ \hline
P0V9 & 0.9V & 10A \\ \hline
P0V95 & 0.95V & 31mA\\ \hline
P1V0 & 1.0V & 3A\\ \hline
P1V2 & 1.2V & 0.6A\\ \hline
P1V5 & 1.5V & 7.5A\\ \hline
P1V8 & 1.8V & 1.6A\\ \hline
P3V3 & 3.3 V & 2A\\ \hline
P3V3MP & 3.3V & 0.18A \\ \hline
P5V0 & 5.0V & 0.5A\\ \hline
\end{longtable}
	
\begin{longtable}{|c|c|c|} \hline
	\multicolumn{3}{|c|}{Maximum RTM voltages and currents}	\\ \hline
	P12V0 & 12V & 3A \\ \hline	
	P3V3MP\_RTM & 3.3V & 30mA \\ \hline
\end{longtable}
	
\subsubsection{Exar parameters}

Exar chip(XR77129) has 4 configurable outputs with configirable current limits. Each channel can be confugured individually. It is possible to set voltage, current limit and power sequencing. In Figure \ref{exar1} we can see that main power supply is 12V, Under Voltage Lockout(UVLO) is set to 6V, so below this value chip will shutdown all channels. When the temperature rise under Over Temperature Protection (OTP) 105 degrees, the chip will generate warning event and restart. \\
All 4 channells can be grouped together and will start-up and shut-down in an user defined sequwnce. Selecting none means channels will not be assigned to any group and therefore, will be controlled independently. Group 0 is controlled by ENABLE or PM\_I2C command. Group 1 can be controlled by GPIO or by PM\_I2C command. By selecting 'Wait PGOOD' next channel will not power up untill current channel reaches the target level. Delay is an additional delay time which postpone after power up one and another channel in group.\\
In on-going Exar configuration - Figure \ref{exar2}, power sequencing looks like this: After Enable from MMC P1V0 start-up, after it reaches proper value, Exar waits 10ms and turn ramp up another channel in this group - P1V8. In the same order is ramp up last channel in this group. Finally on command 'EN\_PSU\_CH' P3V3 ramp up.

	\begin{figure}[htbp!]
		\centering
		\\
		\caption{Exar configuration} \label{exar1}
	\end{figure}
	
	\begin{figure}[htbp!]
		\centering
		\\
		\caption{Exar power on delays} \label{exar2}
	\end{figure}	
	
\clearpage	

%\subsubsection{Exar configuration}
%Exar chips are configured via I2C bus (MUX Port 5) or directly by connecting to W1 (call-out 28) header. For proper configuration \textbf{Exar Power Architect} in version \textbf{5.2-r1} is needed.
%% Configuration files can be found at github in folder \href{https://github.com/m-labs/sinara/tree/master/EXAR\_config}{m-labs/sinara/Exar\_config}\\
%
%\noindent
%\textbf{Exar Power Archtect 5.2-r1:}
%\href{https://www.exar.com/content/document.ashx?id=21632}{https://www.exar.com/content/document.ashx?id=21632}\\
%\textbf{Configuration files:}
%\href{https://github.com/m-labs/sinara/tree/master/EXAR\_config}{https://github.com/m-labs/sinara/tree/master/EXAR\_config}\\
%\textbf{Datasheet:}\href{https://www.exar.com/ds/xr77129_1a_120514.pdf}{https://www.exar.com/ds/xr77129\_1a\_120514.pdf}\\
%\textbf{Quick Start Guide:} \href{https://www.exar.com/files/powerxr/PA5-QSG_110_010614.pdf}{https://www.exar.com/files/powerxr/PA5-QSG\_110\_010614.pdf}\\
%
%
%Actual voltages and current consumption, temperature can be found in Chip Dashboard. There is also oportunity to adjust settings.
%
%	\begin{figure}[htbp!]
%		\centering
%		\includegraphics[scale=0.6]{img/exarprog.png}\\
%		\caption{Chip Dashboard} 
%	\end{figure}
%

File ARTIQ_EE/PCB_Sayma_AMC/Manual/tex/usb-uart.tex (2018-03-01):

\section{USB-UART}
\subsection{USB console switch}

UART from FPGA is connected through Multiplexer (SN74CB3T3257PW). Selection between MMC and USB is preformed automaticly. When micro-USB is connected, +5V from USB bus  switches the multiplexer to pass data from USB to FPGA, after un plugging cable, the switch signal S fall down and the multiplexer conects MMC to FPGA.\\

\begin{itemize}
	\item PRI\_UART is connected to FPGA, configuration is 1N8 115200 baudrate
	\item AUX\_UART is connected to FPGA, configuration is 1N8 115200 baudrate
	\item UART1 is connected to MMC, configuration is 1N8 115200 baudrate
	\item UART4 is connected to MMC, configuration is 1N8 115200 baudrate
	\item MMC\_CONS\_PROG is conected to MMC, configuration is 1N8 115200 baudrate
\end{itemize}

\subsection{USB-UART bridge}

The USB-UART bridge (FT4232H) requires USB device drivers, vailable free from http://www.ftdichip.com,
which are used to make the FT4232H on the Mini Module appear as a four virtual COM ports (VCP). This
then allows the user to communicate with the USB interface via a standard PC serial emulation port
(TTY).\\

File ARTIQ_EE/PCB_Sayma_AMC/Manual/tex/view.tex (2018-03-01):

\section{Product view}	
	
	\begin{figure}[htbp!]
		\centering
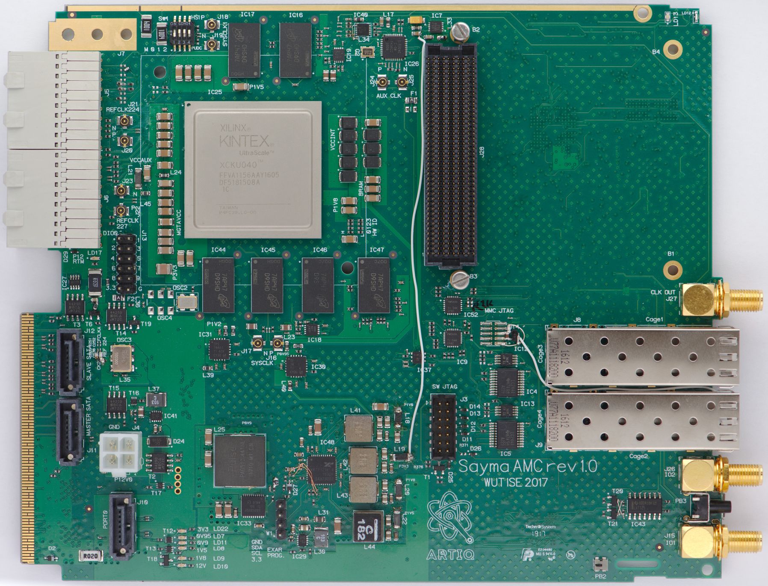
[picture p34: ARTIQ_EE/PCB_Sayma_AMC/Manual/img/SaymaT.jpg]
		\\
		\caption{Top view}
	\end{figure}
	
		\begin{figure}[htbp!]
			\centering
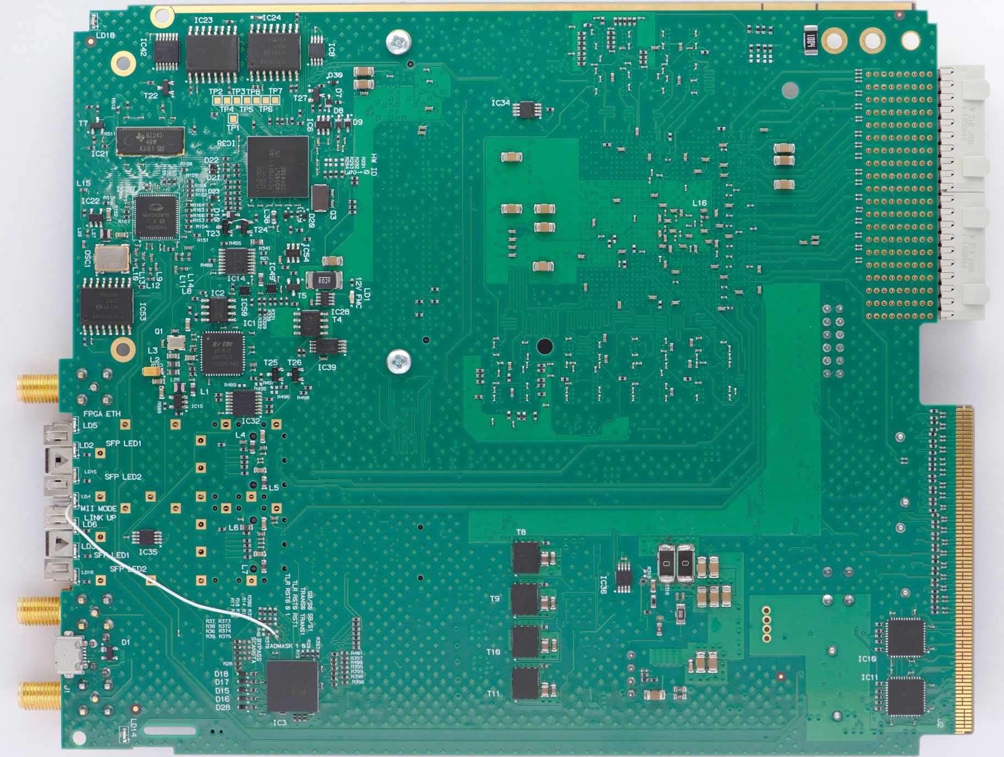
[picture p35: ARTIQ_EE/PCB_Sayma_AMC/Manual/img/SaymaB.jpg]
			\\
			\caption{Bottom view}
		\end{figure}

		\begin{figure}[htbp!]
			\centering
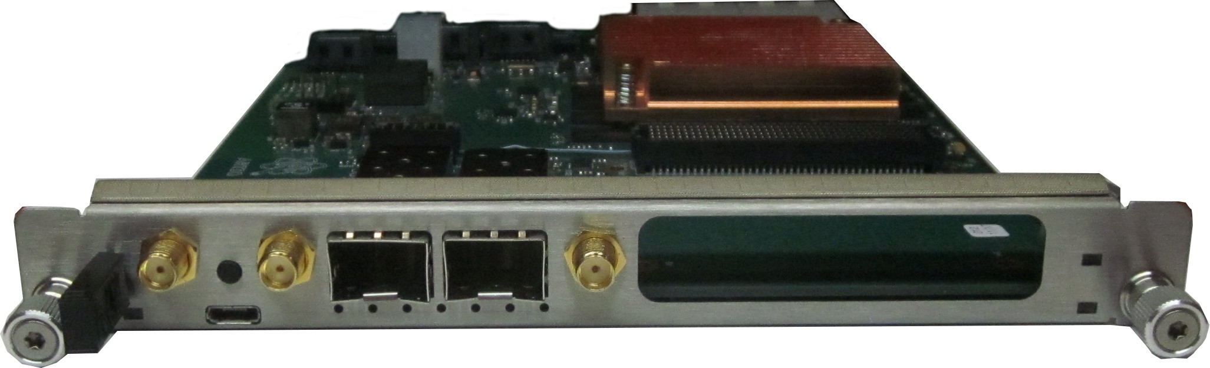
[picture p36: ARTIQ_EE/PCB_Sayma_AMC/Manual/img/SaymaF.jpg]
			\\
			\caption{Front view}
		\end{figure}
	
		\begin{figure}[htbp!]
			\centering
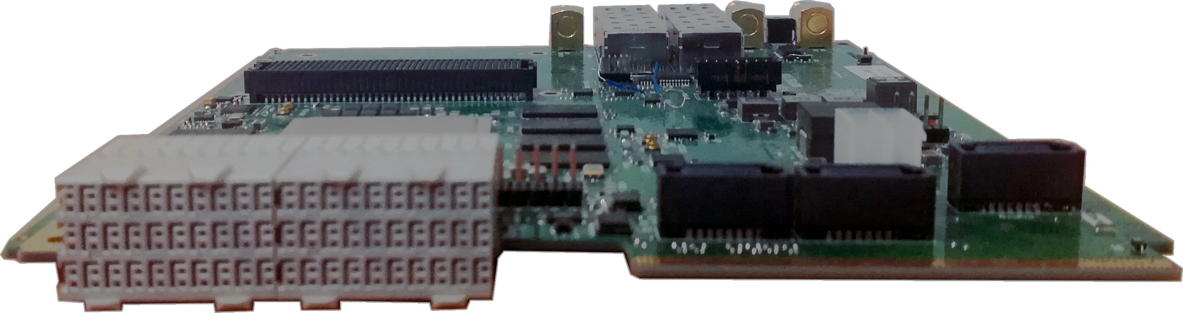
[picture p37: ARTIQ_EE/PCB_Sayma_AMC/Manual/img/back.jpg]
			\\
			\caption{Back view}
		\end{figure}

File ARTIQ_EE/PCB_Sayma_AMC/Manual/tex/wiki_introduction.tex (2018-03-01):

\textbf {\Large Introduction to ARTIQ Sinara}\\

Sinara is an open-source hardware ecosystem originally designed for use
in quantum physics experiments running the
\href{https://m-labs.hk/artiq/}{ARTIQ} control software. It is licensed
under CERN OHL v1.2.

Control electronics used in many trapped-ion and other quantum physics
experiments suffers from a number of problems. In general, an ad-hoc
solution is hastily put together in-house without enough consideration
about good design, reproducibility, testing and documentation. This
makes those systems unreliable, fragile, and difficult to use and
maintain. It also duplicates work in different laboratories. In
addition, the performance and features of the existing systems
(e.g.~regarding pulse shaping abilities) is becoming insufficient for
some experiments.

To alleviate those problems, Sinara aims to be:

\begin{itemize}

\item
  high-quality
\item
  simple to use and ``turn-key''
\item
  reproducible and open
\item
  flexible and modular
\item
  well tested
\item
  well supported by the ARTIQ control software
\end{itemize}

%To see how Sinara can be used in your labs, take a look at our
%\href{CaseStudies}{case studies} showing Sinara in Action.

Sinara is currently developed by a \href{team}{collaboration} including
M-Labs, Warsaw University of Technology (WUT), US Army Research
Laboratory (ARL), the University of Oxford, the University of Maryland
and NIST. The majority of the hardware was designed by WUT. The work was
funded by ARL, Duke University, the University of Oxford, and the
University of Freiburg.\\

%\emph{Currently, much of this hardware is at the prototyping stage.}
%Information about the status of the various hardware projects making up
%Sinara can be found \href{Status}{here}. Advice about purchasing Sinara
%hardware can be found \href{Purchasing}{here}.
%
%\section{Overview}\label{overview}

Following the ARTIQ model, an experiment consists of a core device
(master) -- typically either a \url{Metlino} or \url{Kasli} --
controlling multiple slave devices in real time using ARTIQ's
\href{https://github.com/m-labs/artiq/wiki/DRTIO}{distributed real-time
IO} (DRTIO) protocol. DRTIO provides both gigabit communication links
and time distribution over copper cable or optical fibres. It
synchronises all device clocks, ensuring they have deterministic phase
relationships, and enables nanosecond timing resolution for input and
output events across all devices in the experiment. More detailed
information about communication between devices and time distribution
inside Sinara can be found \href{SinaraClocking}{here}.\\

Sinara uses two main form factors for hardware requiring real-time
control: microTCA (uTCA) and Eurocard Extension Modules (EEM). Non
real-time hardware is typically connected to the host PC using ethernet.\\

MicroTCA (uTCA) is Sinara's preferred form factor for high performance
hardware with high-speed data converters requiring deterministic phase
control, such as the \href{Sayma}{\emph{Sayma}} Smart Arbitrary Waveform
Generator (SAWG). Information about uTCA hardware, including a list of
parts needed to build a Sinara uTCA crate can be found
\href{uTCA}{here}.\\

EEMs provide a lower cost, simpler platform than uTCA for hardware that
requires real-time control, but not bandwidth or complexity of uTCA
hardware.\\

Extension modules connect to a carrier, such as \url{Kasli} or the
\href{VHDCICarrier}{VHDCI carrier}, which provides power and DRTIO. They
are designed to be mounted either in stand-alone enclosures, or in a
rack with a carrier, and connect to the carrier via ribbon cable. More
details about the extension module standard can be found
\href{EEM}{here}.\\

uTCA hardware interfaces with the extension modules either directly,
using a \href{VHDCICarrier}{VHDCI carrier}, or indirectly, using a
\url{Kasli} DRTIO slave.

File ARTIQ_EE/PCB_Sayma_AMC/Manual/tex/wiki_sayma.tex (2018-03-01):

\section{Sayma}

Sayma is a hardware that supports M-Lab's Smart Arbitrary Waveform Generator(\href{http://m-labs.hk/artiq/manual-master/core_drivers_reference.html?highlight=sawg#module-artiq.coredevice.sawg}{SAWG}) gateware.
Provide 8 channels of
1.2 GSPS 16-bit DACs (2.4 GHz DAC clock) and 125 MSPS 16-bit ADCs. It
consists of an AMC, providing the high-speed digital logic, and a RTM,
holding the data converters and analog components.

The design files are located in
\href{https://github.com/m-labs/sinara/tree/master/ARTIQ_EE/PCB_Sayma_AMC}{ARTIQ\_EE/PCB\_Sayma\_AMC}
and
\href{https://github.com/m-labs/sinara/tree/master/ARTIQ_EE/PCB_Sayma_RTM}{ARTIQ\_EE/PCB\_Sayma\_RTM}
and, the AMC schematic is
\href{https://github.com/m-labs/sinara/blob/master/ARTIQ_EE/Sayma_AMC.pdf}{here}
and the RTM schematic is
\href{https://github.com/m-labs/sinara/blob/master/ARTIQ_EE/Sayma_RTM.pdf}{here}.
The PCBs are double width, mid height AMC module. Sayma AMC

\subsection{Features}\label{features}

\begin{itemize}

\item
  May be used in a uTCA rack or stand-alone operation with fibre-based
  DRTIO link
\item
  Analog input and output front-ends provided by plug-in
  \href{https://github.com/m-labs/sinara/wiki/SaymaAFE}{AFE} modules (eg BaseMod) for maximum
  flexibility.
\item
  Extremely flexible \href{https://github.com/m-labs/sinara/wiki/SinaraClocking}{clocking options}
\item
  Flexible feedback to SAWG parameters planned. Specification
  \href{https://github.com/m-labs/sinara/wiki/Servo}{here}.
\end{itemize}

\subsection{Key AMC Components}\label{key-amc-components}

\noindent

\textbf{Programmable resources:}

\begin{itemize}
	\item Xilinx Kintex UltraScale – XCKU040-1FFVA-1156C    FPGA 20 I/O, 530K
	Logic Cells
	\begin{itemize}
		\item speed grade: -1
		\item 20 GTH transceivers (Max Preformance 16.3 Gb/s)
	\end{itemize}
	\item MMC: LPC17762984
\end{itemize}	

\textbf{Memory:}

\begin{itemize}
	\item 512Mb  DDR3 SDRAM (32-bit interface), 800MHz (clock)
	\item 1Gb  DDR3 SDRAM (64-bit interface), 800MHz (clock)
	\item SPI Flash for FPGA configuration. Accessible by MMC
	\item SPI Flash for user data storage
	\item EEPROM with MAC and unique ID 
	
\end{itemize}

\textbf{Connectivity:}

\begin{itemize}
	\item 1 high pin count (HPC) FMC slot for single width mezzanine card
	\item Micro-USB UART connected to FPGA or MMC
	\item Stand-alone 12V power connector 
	\item MGT (Multi-Gigabit Transceiver) connected to:
	\begin{itemize}
		%		\item FMC x1
		\item RTM x16
		\item Fat\_Pipe1 x2
		%		\item AMC P2P x4
		%		\item Port 0 – possibility connected to SATA
		\item SFP x2
	\end{itemize}
	%	\item RTM connector with 8 GTP routed to it. Compatible with Sayma RTM module.
	\item  Port 0 – possibility connected to SATA
	\item RTM connector compatible with Sayma RTM module
	
\end{itemize}

\textbf{Supply:}

\begin{itemize}
	\item Monitoring of voltage and Power supply for RTM 12V and FMC 12V
	\item FMC VADJ fixed to 1V8
	\item Monitoring current of all FMC buses
	\item Stand-alone power connectore
	%	\item Czy Exar monitoruje powera? 
	
\end{itemize}

\textbf{Clocking:}

\begin{itemize}
	\item Clock recovery Si5324  is a precision clock multiplier andjitter attenuator
	\item UFL CLK input
	\item SMA CLK output

\end{itemize}

\textbf{Other:}

\begin{itemize}
	\item Temperature, voltage and current monitoring for critical power buses
	\item Temperature monitoring: FMC1, supply, FPGA core, DDR memory
	\item JTAG multiplexer (SCANSTA) for FMC access, local JTAG port and remote debug/Chipscope via Ethernet
	
\end{itemize}

\subsection{Key RTM Components}\label{key-rtm-components}
\todo[inline]{not sure if it should be here? only in RTM doc?}
\begin{itemize}

\item
  \textbf{DAC}: AD9154 4-channel high-speed data converter

  \begin{itemize}

  \item
    data rate is 1.2 GS/s at 16-bit
  \item
    clock is up to 2.4 GHz (1x, 2x, 4x and 8x interpolating modes)
  \item
    supports mix-mode to emphasize power in 3rd Nyquist Zone
  \item
    interface is 8-lane JESD204B (subclass 1)
  \item
    power consumption is 2.11 W
  \item
    each Sayma has 2 AD9154
  \end{itemize}
\item
  \textbf{ADC}: AD9656 is a 4-channel high-speed digitizer

  \begin{itemize}

  \item
    data rate is 125 MS/s at 16-bit
  \item
    clock is up to 125 MHz
  \item
    650 MHz analog bandwidth
  \item
    interface is 8-lane, 8 Gb/s per lane, JESD204B (subclass 1)
  \item
    each Sayma has 2 AD9656
  \end{itemize}
\item
  \textbf{clock generation}: (summarized \href{SinaraClocking}{here})

  \begin{itemize}

  \item
    Sayma has several distinct clock domains

    \begin{itemize}

    \item
      DAC, JESB204B output clock
    \item
      ADC, JESD204B input clock
    \item
      LO for analog mezzanines
    \end{itemize}
  \item
    These clocks may be generated using a low phase noise
    \href{ClockMezzanines}{Clock Mezzanine} PCB. A single Clock
    Mezzanine can be shared by several Sayma in a uTCA crate using
    {[}Baikal{]} PCB and an RTM RF backplane. Alternately, each Sayma
    can have its own distinct Clock Mezzanine (local generation).
  \end{itemize}
\item
  \textbf{clock distribution}

  \begin{itemize}

  \item
    HMC7043 SPI 14-Output Fanout Buffer for JESD204B
  \item
    HMC830 SPI fractional-N PLL
  \end{itemize}
\item
  \textbf{calibration ADC}: AD7194BCPZ is a 20-bit ADC for
  monitoring/calibration
\end{itemize}

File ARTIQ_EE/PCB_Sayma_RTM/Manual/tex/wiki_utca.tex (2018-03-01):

\section{uTCA.4 Overview}

MicroTCA (uTCA) is Sinara's preferred form-factor for hardware with
high-speed data converters requiring deterministic phase control, such
as the \href{Sayma}{\emph{Sayma}} 2.4 GSPS smart arbitrary waveform
generator (SAWG).

uTCA is a modular, open standard originally developed by the
telecommunications industry. It allows a single rack master -- the Micro
TCA Carrier Hub (MCH) -- to control multiple slave boards, known as
Advanced Mezzanine Cards (AMCs) via a high-speed digital backplane. uTCA
chassis and backplanes are available commercially of the shelf (COTS).

We make use one of the most recent extension to the uTCA standard, uTCA.4.
Originating in the high-energy and particle physics (HEPP) community,
uTCA.4 introduces rear-transition modules (RTMs) along with a second
backplane for low-noise RF signals (RFBP). Each RTM connects to an AMC
(one RTM per AMC). Typically, the AMCs hold FPGAs and other high-speed
digital hardware, communicating with the MCH via gigabit serial links
over the AMC backplane. The RTMs hold data converters and other
low-noise analog components, controlled by the corresponding AMC. The
RFBP provides low-noise clocks and local oscillators (LOs). The RTMs and
RFBP are screened from the AMCs to minimise interference from the
high-speed digital logic.

\begin{figure}[htbp!]
\centering
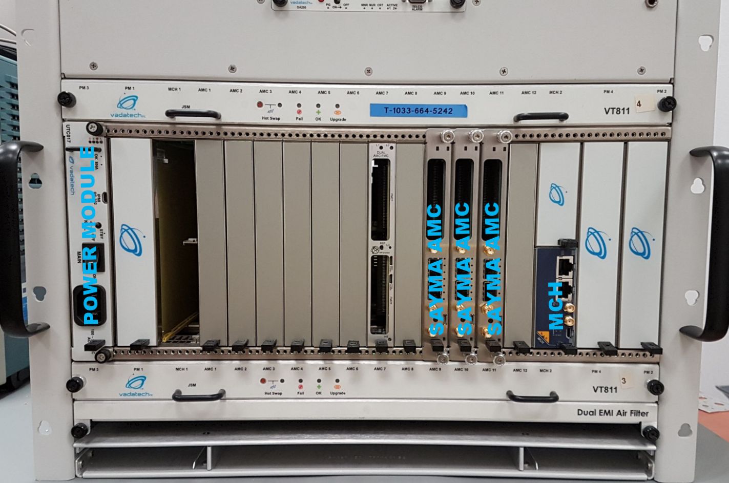
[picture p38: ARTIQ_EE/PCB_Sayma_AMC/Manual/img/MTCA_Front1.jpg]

\caption{Micro TCA chassis with 3 Sayma AMC modules inserted}
\end{figure}

\todo[inline]{New Figure: add photo of Sayma\_AMC attached to Sayma\_RTM sitting on bench so how they're connected is clear.}

(above) Micro TCA chassis with 3 Sayma AMC modules inserted.

Micro TCA chassis with 4 RTM modules inserted. One of them with 4
BaseMod AFE mezzanines installed.

\begin{figure}[htbp!]
\centering
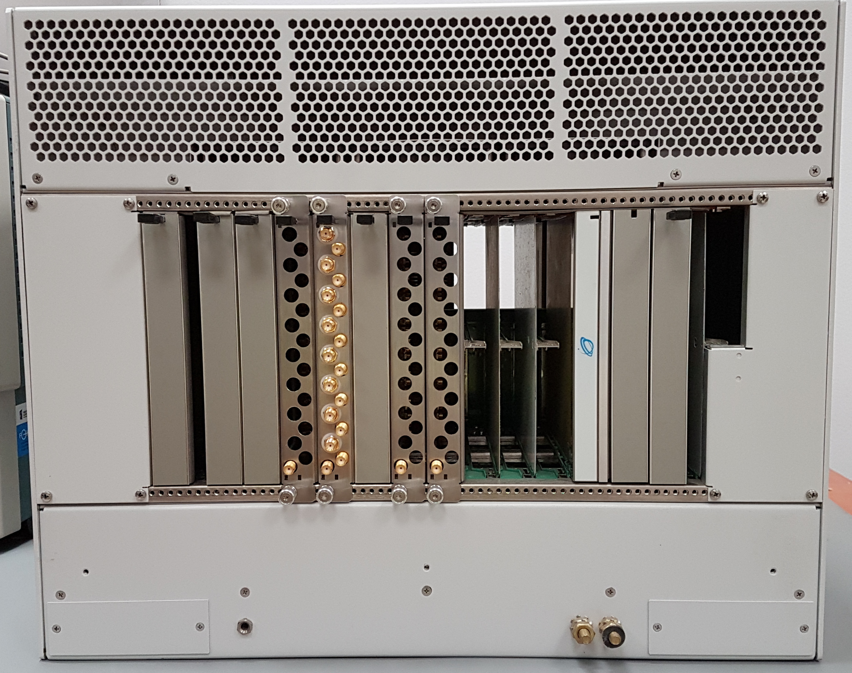
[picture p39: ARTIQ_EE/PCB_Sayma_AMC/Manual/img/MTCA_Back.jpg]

\caption{Micro TCA chassis with 4 RTM modules inserted. One of them has
4 BaseMod AFE mezzanines installed.}
\end{figure}

\href{http://www.nateurope.com/products/NAT-LLRF-Backplane.html}{RF
BP datasheet}

\section{uTCA parts and suppliers}\label{utca-parts-and-suppliers}

\begin{itemize}
\item NAT AC 600D, qty 1
\item NAT MCH-Basic v3.5, mid-size front panel, qty 1
\item NAT Native-R5, qty 1
\end{itemize}

\section{Schematic / Layout Viewer}\label{schematic-layout-viewer}

Hardware was designed under Mentor Graphics Xpedition Enterprise and Altium Designer CAD tools.
Project resources are in two separate folders:
\begin{itemize}
	\item ARTIQ\_EE folder is for designs made with the Mentor Graphics Xpedition Enterprise CAD tool.
	\item ARTIQ\_ALTIUM folder is for designs made with Altium Designer CAD tool.
\end{itemize}
Read-only access to PCB schematics and layout designs is possible using free tools.\\
Mentor has a free tool called
\href{https://www.mentor.com/pcb/downloads/visecad-viewer/}{visECAD
Viewer}.\\
Altium has a free tool called 
\href{http://www.altium.com/altium-designer-viewer}{Altium Designer viewer}

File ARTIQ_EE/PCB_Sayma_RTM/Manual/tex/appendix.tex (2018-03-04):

\section{Total table of signals}

\begin{footnotesize}
	\begin{longtable}{|l|p{6cm}|p{6cm}|}
		\hline
%		\multicolumn{3}{|c|}{\multirow{2}{*}{\textbf{\large{Table 12 - FMC }}}} \\
FPGA ball	&	FPGA signal	&	Signal on the board	\\ \hline

A1	&	GND	&	GND	\\ \hline
A2	&	MGTAVTT	&	MGTAVTT	\\ \hline
A3	&	MGTPRXN1\_216	&	RTM\_FPGA\_GTP\_Rx1\_N	\\ \hline
A4	&	MGTPRXP1\_216	&	RTM\_FPGA\_GTP\_Rx1\_P	\\ \hline
A5	&	GND\_3	&	GND	\\ \hline
A6	&	MGTRREF\_216	&	NC	\\ \hline
A7	&	GND\_4	&	GND	\\ \hline
A8	&	GND\_5	&	GND	\\ \hline
A9	&	IO\_L3N\_T0\_DQS\_AD1N\_15	&	CAL\_ADC\_MCLK1	\\ \hline
A10	&	IO\_L5N\_T0\_AD9N\_15	&	CAL\_ADC\_CSn	\\ \hline
A11	&	GND\_1	&	GND	\\ \hline
A12	&	IO\_L7N\_T1\_AD2N\_15	&	MEZZ3\_IO3	\\ \hline
A13	&	IO\_L8P\_T1\_AD10P\_15	&	MEZZ3\_IO4	\\ \hline
A14	&	IO\_L8N\_T1\_AD10N\_15	&	MEZZ3\_IO5	\\ \hline
A15	&	IO\_L10N\_T1\_AD11N\_15	&	MEZZ3\_IO9	\\ \hline
A16	&	VCCO\_15	&	P3V3F	\\ \hline
A17	&	IO\_L15N\_T2\_DQS\_ADV\_B\_15	&	HMC\_SPI\_SCLK	\\ \hline
A18	&	GND\_2	&	GND	\\ \hline
B1	&	MGTPTXN3\_216	&	RTM\_FPGA\_GTP\_Tx3C\_N	\\ \hline
B2	&	MGTPTXP3\_216	&	RTM\_FPGA\_GTP\_Tx3C\_P	\\ \hline
B3	&	GND\_7	&	GND	\\ \hline
B4	&	MGTAVCC	&	MGTAVCC	\\ \hline
B5	&	MGTREFCLK1N\_216	&	CDR\_CLK\_CLEAN1\_N	\\ \hline
B6	&	MGTREFCLK1P\_216	&	CDR\_CLK\_CLEAN1\_P	\\ \hline
B7	&	GND\_8	&	GND	\\ \hline
B8	&	GND\_9	&	GND	\\ \hline
B9	&	IO\_L3P\_T0\_DQS\_AD1P\_15	&	CAL\_ADC\_MCLK2	\\ \hline
B10	&	IO\_L5P\_T0\_AD9P\_15	&	CAL\_ADC\_SYNCn	\\ \hline
B11	&	IO\_L4N\_T0\_15	&	CAL\_ADC\_DIN	\\ \hline
B12	&	IO\_L7P\_T1\_AD2P\_15	&	MEZZ3\_IO2	\\ \hline
B13	&	VCCO\_15\_1	&	P3V3F	\\ \hline
B14	&	IO\_L10P\_T1\_AD11P\_15	&	MEZZ3\_IO8	\\ \hline
B15	&	IO\_L9N\_T1\_DQS\_AD3N\_15	&	MEZZ3\_IO7	\\ \hline
B16	&	IO\_L15P\_T2\_DQS\_15	&	HMC\_SPI\_SDATA	\\ \hline
B17	&	IO\_L16N\_T2\_A27\_15	&	USR\_UART\_N	\\ \hline
B18	&	GND\_6	&	GND	\\ \hline
C1	&	MGTAVTT\_1	&	MGTAVTT	\\ \hline
C2	&	GND\_11	&	GND	\\ \hline
C3	&	MGTPRXN2\_216	&	RTM\_FPGA\_GTP\_Rx2\_N	\\ \hline
C4	&	MGTPRXP2\_216	&	RTM\_FPGA\_GTP\_Rx2\_P	\\ \hline
C5	&	MGTAVCC\_1	&	MGTAVCC	\\ \hline
C6	&	GND\_12	&	GND	\\ \hline
C7	&	GND\_13	&	GND	\\ \hline
C8	&	IO\_L1N\_T0\_AD0N\_15	&	HMC830\_SPI\_SEN	\\ \hline
C9	&	IO\_L2N\_T0\_AD8N\_15	&	CAL\_ADC\_SCLK	\\ \hline
C10	&	VCCO\_15\_2	&	P3V3F	\\ \hline
C11	&	IO\_L4P\_T0\_15	&	CAL\_ADC\_DOUT	\\ \hline
C12	&	IO\_L6N\_T0\_VREF\_15	&	MEZZ3\_IO1	\\ \hline
C13	&	IO\_L11N\_T1\_SRCC\_15	&	MEZZ3\_IO11	\\ \hline
C14	&	IO\_L9P\_T1\_DQS\_AD3P\_15	&	MEZZ3\_IO6	\\ \hline
C15	&	GND\_10	&	GND	\\ \hline
C16	&	IO\_L16P\_T2\_A28\_15	&	USR\_UART\_P	\\ \hline
C17	&	IO\_L18P\_T2\_A24\_15	&	CLK\_MEZZ\_IO1	\\ \hline
C18	&	IO\_L18N\_T2\_A23\_15	&	CLK\_MEZZ\_IO2	\\ \hline
D1	&	MGTPTXN2\_216	&	RTM\_FPGA\_GTP\_Tx2C\_N	\\ \hline
D2	&	MGTPTXP2\_216	&	RTM\_FPGA\_GTP\_Tx2C\_P	\\ \hline
D3	&	GND\_15	&	GND	\\ \hline
D4	&	GND\_16	&	GND	\\ \hline
D5	&	MGTREFCLK0N\_216	&	RTM\_FPGA\_GTP\_CLKC\_P	\\ \hline
D6	&	MGTREFCLK0P\_216	&	RTM\_FPGA\_GTP\_CLKC\_N	\\ \hline
D7	&	GND\_17	&	GND	\\ \hline
D8	&	IO\_L1P\_T0\_AD0P\_15	&	HMC\_SPI\_GPIO	\\ \hline
D9	&	IO\_L2P\_T0\_AD8P\_15	&	HMC\_SPI\_SDO	\\ \hline
D10	&	IO\_0\_15	&	SI5324\_INT\_ALM	\\ \hline
D11	&	IO\_L6P\_T0\_15	&	MEZZ3\_IO0	\\ \hline
D12	&	GND\_14	&	GND	\\ \hline
D13	&	IO\_L11P\_T1\_SRCC\_15	&	MEZZ3\_IO10	\\ \hline
D14	&	IO\_L12N\_T1\_MRCC\_15	&	MEZZ3\_IO13	\\ \hline
D15	&	IO\_L13N\_T2\_MRCC\_15	&	MEZZ3\_IO14	\\ \hline
D16	&	IO\_L14N\_T2\_SRCC\_15	&	HMC7043\_SLEN	\\ \hline
D17	&	VCCO\_15\_3	&	P3V3F	\\ \hline
D18	&	IO\_L17N\_T2\_A25\_15	&	CLK\_MEZZ\_IO0	\\ \hline
E1	&	MGTAVTT\_2	&	MGTAVTT	\\ \hline
E2	&	GND\_18	&	GND	\\ \hline
E3	&	MGTPRXN0\_216	&	RTM\_FPGA\_GTP\_Rx0\_N	\\ \hline
E4	&	MGTPRXP0\_216	&	RTM\_FPGA\_GTP\_Rx0\_P	\\ \hline
E5	&	MGTAVCC\_2	&	MGTAVCC	\\ \hline
E6	&	GND\_19	&	GND	\\ \hline
E7	&	GND\_20	&	GND	\\ \hline
E8	&	CCLK\_0	&	FPGA\_CFG\_CCLK	\\ \hline
E9	&	GND\_21	&	GND	\\ \hline
E10	&	VCCO\_0	&	P3V3F	\\ \hline
E11	&	VCCBATT\_0	&	P1V8F	\\ \hline
E12	&	CFGBVS\_0	&	NC	\\ \hline
E13	&	IO\_L12P\_T1\_MRCC\_15	&	MEZZ3\_IO12	\\ \hline
E14	&	VCCO\_15\_4	&	P3V3F	\\ \hline
E15	&	IO\_L13P\_T2\_MRCC\_15	&	NC	\\ \hline
E16	&	IO\_L14P\_T2\_SRCC\_15	&	MEZZ3\_IO15	\\ \hline
E17	&	IO\_L17P\_T2\_A26\_15	&	SI5324\_RST	\\ \hline
E18	&	IO\_L24N\_T3\_RS0\_15	&	CLK\_MEZZ\_IO15	\\ \hline
F1	&	MGTPTXN1\_216	&	RTM\_FPGA\_GTP\_Tx1C\_N	\\ \hline
F2	&	MGTPTXP1\_216	&	RTM\_FPGA\_GTP\_Tx1C\_P	\\ \hline
F3	&	MGTAVTT\_3	&	MGTAVTT	\\ \hline
F4	&	GND\_24	&	GND	\\ \hline
F5	&	MGTAVCC\_3	&	MGTAVCC	\\ \hline
F6	&	GND\_25	&	GND	\\ \hline
F7	&	VCCINT	&	P1V0	\\ \hline
F8	&	TCK\_0	&	TCK	\\ \hline
F9	&	VCCINT\_1	&	P1V0	\\ \hline
F10	&	GND\_22	&	GND	\\ \hline
F11	&	VCCBRAM	&	VCCBRAM	\\ \hline
F12	&	DONE\_0	&	FPGA\_CFG\_DONE	\\ \hline
F13	&	M2\_0	&	NC	\\ \hline
F14	&	IO\_L22N\_T3\_A16\_15	&	CLK\_MEZZ\_IO10	\\ \hline
F15	&	IO\_L21N\_T3\_DQS\_A18\_15	&	CLK\_MEZZ\_IO8	\\ \hline
F16	&	GND\_23	&	GND	\\ \hline
F17	&	IO\_L24P\_T3\_RS1\_15	&	CLK\_MEZZ\_IO13	\\ \hline
F18	&	IO\_L19N\_T3\_A21\_VREF\_15	&	CLK\_MEZZ\_IO4	\\ \hline
G1	&	GND\_26	&	GND	\\ \hline
G2	&	MGTAVTT\_4	&	MGTAVTT	\\ \hline
G3	&	MGTPRXN3\_216	&	RTM\_FPGA\_GTP\_Rx3\_N	\\ \hline
G4	&	MGTPRXP3\_216	&	RTM\_FPGA\_GTP\_Rx3\_P	\\ \hline
G5	&	GND\_29	&	GND	\\ \hline
G6	&	GND\_30	&	GND	\\ \hline
G7	&	GND\_31	&	GND	\\ \hline
G8	&	VCCINT\_2	&	P1V0	\\ \hline
G9	&	GND\_32	&	GND	\\ \hline
G10	&	VCCBRAM\_1	&	VCCBRAM	\\ \hline
G11	&	GND\_27	&	GND	\\ \hline
G12	&	VCCAUX	&	VCCAUX	\\ \hline
G13	&	GND\_28	&	GND	\\ \hline
G14	&	IO\_L22P\_T3\_A17\_15	&	CLK\_MEZZ\_IO9	\\ \hline
G15	&	IO\_L21P\_T3\_DQS\_15	&	CLK\_MEZZ\_IO7	\\ \hline
G16	&	IO\_L20N\_T3\_A19\_15	&	CLK\_MEZZ\_IO6	\\ \hline
G17	&	IO\_L19P\_T3\_A22\_15	&	CLK\_MEZZ\_IO3	\\ \hline
G18	&	VCCO\_15\_5	&	P3V3F	\\ \hline
H1	&	MGTPTXN0\_216	&	RTM\_FPGA\_GTP\_Tx0C\_N	\\ \hline
H2	&	MGTPTXP0\_216	&	RTM\_FPGA\_GTP\_Tx0C\_P	\\ \hline
H3	&	GND\_35	&	GND	\\ \hline
H4	&	GND\_36	&	GND	\\ \hline
H5	&	GND\_37	&	GND	\\ \hline
H6	&	GND\_38	&	GND	\\ \hline
H7	&	VCCINT\_3	&	P1V0	\\ \hline
H8	&	GND\_39	&	GND	\\ \hline
H9	&	VCCINT\_4	&	P1V0	\\ \hline
H10	&	GND\_33	&	GND	\\ \hline
H11	&	VCCBRAM\_2	&	VCCBRAM	\\ \hline
H12	&	GND\_34	&	GND	\\ \hline
H13	&	VCCAUX\_1	&	VCCAUX	\\ \hline
H14	&	IO\_25\_15	&	CLK\_MEZZ\_IO14	\\ \hline
H15	&	VCCO\_15\_6	&	P3V3F	\\ \hline
H16	&	IO\_L20P\_T3\_A20\_15	&	CLK\_MEZZ\_IO5	\\ \hline
H17	&	IO\_L23P\_T3\_FOE\_B\_15	&	CLK\_MEZZ\_IO11	\\ \hline
H18	&	IO\_L23N\_T3\_FWE\_B\_15	&	CLK\_MEZZ\_IO12	\\ \hline
J1	&	GND\_40	&	GND	\\ \hline
J2	&	GND\_44	&	GND	\\ \hline
J3	&	GND\_45	&	GND	\\ \hline
J4	&	IO\_L2N\_T0\_34	&	MEZZ4\_IO2	\\ \hline
J5	&	IO\_L2P\_T0\_34	&	MEZZ4\_IO1	\\ \hline
J6	&	IO\_0\_34	&	RTM\_FPGA\_SCL	\\ \hline
J7	&	GND\_46	&	GND	\\ \hline
J8	&	VCCINT\_6	&	P1V0	\\ \hline
J9	&	GNDADC\_0	&	NC	\\ \hline
J10	&	VCCADC\_0	&	NC	\\ \hline
J11	&	GND\_41	&	GND	\\ \hline
J12	&	VCCINT\_5	&	P1V0	\\ \hline
J13	&	GND\_42	&	GND	\\ \hline
J14	&	IO\_L5P\_T0\_D06\_14	&	REF\_CLK\_SRC\_SEL\_1V8	\\ \hline
J15	&	IO\_L2P\_T0\_D02\_14	&	DAC2\_SPI\_SDIO	\\ \hline
J16	&	IO\_L2N\_T0\_D03\_14	&	DAC2\_SPI\_SDO	\\ \hline
J17	&	GND\_43	&	GND	\\ \hline
J18	&	IO\_L3P\_T0\_DQS\_PUDC\_B\_14	&	DAC2\_SPI\_SCLK	\\ \hline
K1	&	IO\_L3N\_T0\_DQS\_34	&	MEZZ4\_IO4	\\ \hline
K2	&	IO\_L3P\_T0\_DQS\_34	&	MEZZ4\_IO3	\\ \hline
K3	&	IO\_L4P\_T0\_34	&	MEZZ4\_IO5	\\ \hline
K4	&	GND\_49	&	GND	\\ \hline
K5	&	IO\_L1N\_T0\_34	&	MEZZ4\_IO0	\\ \hline
K6	&	IO\_L1P\_T0\_34	&	RTM\_FPGA\_SDA	\\ \hline
K7	&	VCCINT\_8	&	P1V0	\\ \hline
K8	&	GND\_50	&	GND	\\ \hline
K9	&	VREFN\_0	&	NC	\\ \hline
K10	&	VP\_0	&	NC	\\ \hline
K11	&	VCCINT\_7	&	P1V0	\\ \hline
K12	&	GND\_47	&	GND	\\ \hline
K13	&	VCCAUX\_2	&	VCCAUX	\\ \hline
K14	&	GND\_48	&	GND	\\ \hline
K15	&	IO\_L5N\_T0\_D07\_14	&	NC	\\ \hline
K16	&	IO\_L1P\_T0\_D00\_MOSI\_14	&	NC	\\ \hline
K17	&	IO\_L4P\_T0\_D04\_14	&	DAC2\_IRQn	\\ \hline
K18	&	IO\_L3N\_T0\_DQS\_EMCCLK\_14	&	DAC2\_SPI\_CSn	\\ \hline
L1	&	GND\_51	&	GND	\\ \hline
L2	&	IO\_L4N\_T0\_34	&	MEZZ4\_IO6	\\ \hline
L3	&	IO\_L5N\_T0\_34	&	MEZZ4\_IO8	\\ \hline
L4	&	IO\_L5P\_T0\_34	&	MEZZ4\_IO7	\\ \hline
L5	&	IO\_L6P\_T0\_34	&	MEZZ4\_IO9	\\ \hline
L6	&	VCCO\_34	&	P3V3F	\\ \hline
L7	&	GND\_54	&	GND	\\ \hline
L8	&	VCCINT\_10	&	P1V0	\\ \hline
L9	&	VN\_0	&	NC	\\ \hline
L10	&	VREFP\_0	&	NC	\\ \hline
L11	&	GND\_52	&	GND	\\ \hline
L12	&	VCCINT\_9	&	P1V0	\\ \hline
L13	&	GND\_53	&	GND	\\ \hline
L14	&	IO\_0\_14	&	DAC2\_TXEN1	\\ \hline
L15	&	IO\_L6P\_T0\_FCS\_B\_14	&	DIO7	\\ \hline
L16	&	VCCO\_14	&	P1V8F	\\ \hline
L17	&	IO\_L1N\_T0\_D01\_DIN\_14	&	DAC2\_TXEN0	\\ \hline
L18	&	IO\_L4N\_T0\_D05\_14	&	REF\_LO\_CLK\_SEL\_1V8	\\ \hline
M1	&	IO\_L7N\_T1\_34	&	MEZZ4\_IO12	\\ \hline
M2	&	IO\_L7P\_T1\_34	&	MEZZ4\_IO11	\\ \hline
M3	&	VCCO\_34\_1	&	P3V3F	\\ \hline
M4	&	IO\_L10P\_T1\_34	&	MEZZ1\_IO1	\\ \hline
M5	&	IO\_L6N\_T0\_VREF\_34	&	MEZZ4\_IO10	\\ \hline
M6	&	IO\_L8P\_T1\_34	&	MEZZ4\_IO13	\\ \hline
M7	&	VCCINT\_12	&	P1V0	\\ \hline
M8	&	GND\_57	&	GND	\\ \hline
M9	&	DXN\_0	&	FPGA\_DXN	\\ \hline
M10	&	DXP\_0	&	FPGA\_DXP	\\ \hline
M11	&	VCCINT\_11	&	P1V0	\\ \hline
M12	&	GND\_55	&	GND	\\ \hline
M13	&	VCCAUX\_3	&	VCCAUX	\\ \hline
M14	&	IO\_L8P\_T1\_D11\_14	&	DIO5	\\ \hline
M15	&	IO\_L6N\_T0\_D08\_VREF\_14	&	DIO6	\\ \hline
M16	&	IO\_L7P\_T1\_D09\_14	&	REC\_CLOCK\_P\_1	\\ \hline
M17	&	IO\_L7N\_T1\_D10\_14	&	REC\_CLOCK\_N\_1	\\ \hline
M18	&	GND\_56	&	GND	\\ \hline
N1	&	IO\_L9P\_T1\_DQS\_34	&	MEZZ4\_IO15	\\ \hline
N2	&	IO\_L11N\_T1\_SRCC\_34	&	MEZZ1\_IO4	\\ \hline
N3	&	IO\_L11P\_T1\_SRCC\_34	&	MEZZ1\_IO3	\\ \hline
N4	&	IO\_L10N\_T1\_34	&	MEZZ1\_IO2	\\ \hline
N5	&	GND\_61	&	GND	\\ \hline
N6	&	IO\_L8N\_T1\_34	&	MEZZ4\_IO14	\\ \hline
N7	&	GND\_62	&	GND	\\ \hline
N8	&	VCCINT\_15	&	P1V0	\\ \hline
N9	&	GND\_63	&	GND	\\ \hline
N10	&	VCCINT\_13	&	P1V0	\\ \hline
N11	&	GND\_58	&	GND	\\ \hline
N12	&	VCCINT\_14	&	P1V0	\\ \hline
N13	&	GND\_59	&	GND	\\ \hline
N14	&	IO\_L8N\_T1\_D12\_14	&	DIO4	\\ \hline
N15	&	GND\_60	&	GND	\\ \hline
N16	&	IO\_L9P\_T1\_DQS\_14	&	DIO3	\\ \hline
N17	&	IO\_L9N\_T1\_DQS\_D13\_14	&	DIO2	\\ \hline
N18	&	IO\_L10P\_T1\_D14\_14	&	DIO1	\\ \hline
P1	&	IO\_L9N\_T1\_DQS\_34	&	MEZZ1\_IO0	\\ \hline
P2	&	GND\_65	&	GND	\\ \hline
P3	&	IO\_L12N\_T1\_MRCC\_34	&	MEZZ1\_IO6	\\ \hline
P4	&	IO\_L12P\_T1\_MRCC\_34	&	MEZZ1\_IO5	\\ \hline
P5	&	IO\_L19N\_T3\_VREF\_34	&	MEZZ2\_IO4	\\ \hline
P6	&	IO\_L19P\_T3\_34	&	MEZZ2\_IO3	\\ \hline
P7	&	VCCO\_34\_2	&	P3V3F	\\ \hline
P8	&	GND\_66	&	GND	\\ \hline
P9	&	VCCINT\_17	&	P1V0	\\ \hline
P10	&	PROGRAM\_B\_0	&	FPGA\_CFG\_PROGRAM\_B	\\ \hline
P11	&	VCCINT\_16	&	P1V0	\\ \hline
P12	&	GND\_64	&	GND	\\ \hline
P13	&	VCCAUX\_4	&	VCCAUX	\\ \hline
P14	&	IO\_L12P\_T1\_MRCC\_14	&	RTM\_MASTER\_AUX\_CLK\_P	\\ \hline
P15	&	IO\_L11P\_T1\_SRCC\_14	&	REF\_CLK\_SRC\_EXT\_SEL\_1V8	\\ \hline
P16	&	IO\_L11N\_T1\_SRCC\_14	&	DAC\_CLK\_SRC\_SEL\_1V8	\\ \hline
P17	&	VCCO\_14\_1	&	P1V8F	\\ \hline
P18	&	IO\_L10N\_T1\_D15\_14	&	DIO0	\\ \hline
R1	&	IO\_L13N\_T2\_MRCC\_34	&	MEZZ1\_IO8	\\ \hline
R2	&	IO\_L13P\_T2\_MRCC\_34	&	MEZZ1\_IO7	\\ \hline
R3	&	IO\_L14P\_T2\_SRCC\_34	&	MEZZ1\_IO9	\\ \hline
R4	&	VCCO\_34\_3	&	P3V3F	\\ \hline
R5	&	IO\_L21P\_T3\_DQS\_34	&	MEZZ2\_IO7	\\ \hline
R6	&	IO\_25\_34	&	MEZZ2\_IO15	\\ \hline
R7	&	IO\_L22P\_T3\_34	&	MEZZ2\_IO9	\\ \hline
R8	&	TMS\_0	&	TMS	\\ \hline
R9	&	GND\_67	&	GND	\\ \hline
R10	&	VCCO\_0\_1	&	P3V3F	\\ \hline
R11	&	M1\_0	&	NC	\\ \hline
R12	&	M0\_0	&	NC	\\ \hline
R13	&	IO\_L19P\_T3\_A10\_D26\_14	&	DAC1\_SPI\_SDO	\\ \hline
R14	&	VCCO\_14\_2	&	P1V8F	\\ \hline
R15	&	IO\_L12N\_T1\_MRCC\_14	&	RTM\_MASTER\_AUX\_CLK\_N	\\ \hline
R16	&	IO\_L14P\_T2\_SRCC\_14	&	RTM\_FPGA\_LVDS1\_P	\\ \hline
R17	&	IO\_L14N\_T2\_SRCC\_14	&	RTM\_FPGA\_LVDS1\_N	\\ \hline
R18	&	IO\_L15P\_T2\_DQS\_RDWR\_B\_14	&	RTM\_FPGA\_USR\_IO\_P	\\ \hline
T1	&	VCCO\_34\_4	&	P3V3F	\\ \hline
T2	&	IO\_L14N\_T2\_SRCC\_34	&	MEZZ1\_IO10	\\ \hline
T3	&	IO\_L17N\_T2\_34	&	MEZZ2\_IO0	\\ \hline
T4	&	IO\_L17P\_T2\_34	&	MEZZ1\_IO15	\\ \hline
T5	&	IO\_L21N\_T3\_DQS\_34	&	MEZZ2\_IO8	\\ \hline
T6	&	GND\_69	&	GND	\\ \hline
T7	&	IO\_L22N\_T3\_34	&	MEZZ2\_IO10	\\ \hline
T8	&	TDO\_0	&	TDO	\\ \hline
T9	&	TDI\_0	&	TDI	\\ \hline
T10	&	INIT\_B\_0	&	FPGA\_CFG\_INIT\_B	\\ \hline
T11	&	VCCO\_14\_3	&	P1V8F	\\ \hline
T12	&	IO\_L22P\_T3\_A05\_D21\_14	&	ADC2\_CSB	\\ \hline
T13	&	IO\_L19N\_T3\_A09\_D25\_VREF\_14	&	DAC1\_SPI\_SCLK	\\ \hline
T14	&	IO\_L13P\_T2\_MRCC\_14	&	CDR\_CLK\_CLEAN2\_P	\\ \hline
T15	&	IO\_L13N\_T2\_MRCC\_14	&	CDR\_CLK\_CLEAN2\_N	\\ \hline
T16	&	GND\_68	&	GND	\\ \hline
T17	&	IO\_L16P\_T2\_CSI\_B\_14	&	RTM\_FPGA\_LVDS2\_P	\\ \hline
T18	&	IO\_L15N\_T2\_DQS\_DOUT\_CSO\_B\_14	&	RTM\_FPGA\_USR\_IO\_N	\\ \hline
U1	&	IO\_L15N\_T2\_DQS\_34	&	MEZZ1\_IO12	\\ \hline
U2	&	IO\_L15P\_T2\_DQS\_34	&	MEZZ1\_IO11	\\ \hline
U3	&	GND\_71	&	GND	\\ \hline
U4	&	IO\_L18P\_T2\_34	&	MEZZ2\_IO1	\\ \hline
U5	&	IO\_L20N\_T3\_34	&	MEZZ2\_IO6	\\ \hline
U6	&	IO\_L20P\_T3\_34	&	MEZZ2\_IO5	\\ \hline
U7	&	IO\_L23P\_T3\_34	&	MEZZ2\_IO11	\\ \hline
U8	&	VCCO\_14\_5	&	P1V8F	\\ \hline
U9	&	IO\_L24P\_T3\_A01\_D17\_14	&	ADC1\_CSB	\\ \hline
U10	&	IO\_25\_14	&	ADC1\_SDIO	\\ \hline
U11	&	IO\_L23P\_T3\_A03\_D19\_14	&	ADC1\_SYNC	\\ \hline
U12	&	IO\_L22N\_T3\_A04\_D20\_14	&	ADC2\_SDIO	\\ \hline
U13	&	GND\_70	&	GND	\\ \hline
U14	&	IO\_L20P\_T3\_A08\_D24\_14	&	DAC1\_SPI\_CSn	\\ \hline
U15	&	IO\_L17P\_T2\_A14\_D30\_14	&	DAC2\_RESETn	\\ \hline
U16	&	IO\_L17N\_T2\_A13\_D29\_14	&	DAC1\_TXEN1	\\ \hline
U17	&	IO\_L16N\_T2\_A15\_D31\_14	&	RTM\_FPGA\_LVDS2\_N	\\ \hline
U18	&	VCCO\_14\_4	&	P1V8F	\\ \hline
V1	&	GND\_72	&	GND	\\ \hline
V2	&	IO\_L16N\_T2\_34	&	MEZZ1\_IO14	\\ \hline
V3	&	IO\_L16P\_T2\_34	&	MEZZ1\_IO13	\\ \hline
V4	&	IO\_L18N\_T2\_34	&	MEZZ2\_IO2	\\ \hline
V5	&	VCCO\_34\_5	&	P3V3F	\\ \hline
V6	&	IO\_L23N\_T3\_34	&	MEZZ2\_IO12	\\ \hline
V7	&	IO\_L24N\_T3\_34	&	MEZZ2\_IO14	\\ \hline
V8	&	IO\_L24P\_T3\_34	&	MEZZ2\_IO13	\\ \hline
V9	&	IO\_L24N\_T3\_A00\_D16\_14	&	ADC2\_PDWN	\\ \hline
V10	&	GND\_73	&	GND	\\ \hline
V11	&	IO\_L23N\_T3\_A02\_D18\_14	&	ADC1\_SCLK	\\ \hline
V12	&	IO\_L21P\_T3\_DQS\_14	&	ADC2\_SYNC	\\ \hline
V13	&	IO\_L21N\_T3\_DQS\_A06\_D22\_14	&	ADC2\_SCLK	\\ \hline
V14	&	IO\_L20N\_T3\_A07\_D23\_14	&	DAC1\_IRQn	\\ \hline
V15	&	VCCO\_14\_6	&	P1V8F	\\ \hline
V16	&	IO\_L18P\_T2\_A12\_D28\_14	&	DAC1\_TXEN0	\\ \hline
V17	&	IO\_L18N\_T2\_A11\_D27\_14	&	DAC1\_SPI\_SDIO	\\ \hline
V18	&	GND\_74	&	GND	\\ \hline

\end{longtable}
\end{footnotesize}

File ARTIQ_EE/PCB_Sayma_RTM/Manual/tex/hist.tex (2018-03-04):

\begin{table}[h!]
\vspace{5cm}
	\centering
	\begin{center}
\begin{tabular}{|l|l|}
	\hline
	\textbf{\rule[-2ex]{0pt}{5.5ex} Document version:} & Preliminary   \\ \hline
\textbf{\rule[-2ex]{0pt}{5.5ex} Issue Date:} & \today         \\ \hline
\textbf{\rule[-2ex]{0pt}{5.5ex} Written by:}      &  Filip Świtakowski                       \\ \hline
\textbf{\rule[-2ex]{0pt}{5.5ex} Approved by:}     &         ---------------      \\ \hline
	\textbf{\rule[-2ex]{0pt}{5.5ex} Document title:}  &  \nazwa - specification \\ \hline

\end{tabular} 
\end{center}
\end{table}

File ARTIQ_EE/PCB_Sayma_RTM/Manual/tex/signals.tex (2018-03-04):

\section{Signal tables}
%---------------------------------------------------------SFP1
\begin{footnotesize}
	\begin{longtable}{|l|p{6cm}|p{6cm}|}
	\hline
	\multicolumn{3}{|c|}{\multirow{2}{*}{\textbf{\large{RTM}}}}\\
	\multicolumn{3}{|c|}{} \\ \hline 
	E3	&	MGTPRXN0\_216	&	RTM\_FPGA\_GTP\_Rx0\_N	\\ \hline
	E4	&	MGTPRXP0\_216	&	RTM\_FPGA\_GTP\_Rx0\_P	\\ \hline
	H1	&	MGTPTXN0\_216	&	RTM\_FPGA\_GTP\_Tx0C\_N	\\ \hline
	H2	&	MGTPTXP0\_216	&	RTM\_FPGA\_GTP\_Tx0C\_P	\\ \hline
	A3	&	MGTPRXN1\_216	&	RTM\_FPGA\_GTP\_Rx1\_N	\\ \hline
	A4	&	MGTPRXP1\_216	&	RTM\_FPGA\_GTP\_Rx1\_P	\\ \hline
	F1	&	MGTPTXN1\_216	&	RTM\_FPGA\_GTP\_Tx1C\_N	\\ \hline
	F2	&	MGTPTXP1\_216	&	RTM\_FPGA\_GTP\_Tx1C\_P	\\ \hline
	C3	&	MGTPRXN2\_216	&	RTM\_FPGA\_GTP\_Rx2\_N	\\ \hline
	C4	&	MGTPRXP2\_216	&	RTM\_FPGA\_GTP\_Rx2\_P	\\ \hline
	D1	&	MGTPTXN2\_216	&	RTM\_FPGA\_GTP\_Tx2C\_N	\\ \hline
	D2	&	MGTPTXP2\_216	&	RTM\_FPGA\_GTP\_Tx2C\_P	\\ \hline
	G3	&	MGTPRXN3\_216	&	RTM\_FPGA\_GTP\_Rx3\_N	\\ \hline
	G4	&	MGTPRXP3\_216	&	RTM\_FPGA\_GTP\_Rx3\_P	\\ \hline
	B1	&	MGTPTXN3\_216	&	RTM\_FPGA\_GTP\_Tx3C\_N	\\ \hline
	B2	&	MGTPTXP3\_216	&	RTM\_FPGA\_GTP\_Tx3C\_P	\\ \hline
	D5	&	MGTREFCLK0N\_216	&	RTM\_FPGA\_GTP\_CLKC\_P	\\ \hline
	D6	&	MGTREFCLK0P\_216	&	RTM\_FPGA\_GTP\_CLKC\_N	\\ \hline
	J6	&	IO\_0\_34	&	RTM\_FPGA\_SCL	\\ \hline
	K6	&	IO\_L1P\_T0\_34	&	RTM\_FPGA\_SDA	\\ \hline
	P14	&	IO\_L12P\_T1\_MRCC\_14	&	RTM\_MASTER\_AUX\_CLK\_P	\\ \hline
	R15	&	IO\_L12N\_T1\_MRCC\_14	&	RTM\_MASTER\_AUX\_CLK\_N	\\ \hline
	R16	&	IO\_L14P\_T2\_SRCC\_14	&	RTM\_FPGA\_LVDS1\_P	\\ \hline
	R17	&	IO\_L14N\_T2\_SRCC\_14	&	RTM\_FPGA\_LVDS1\_N	\\ \hline
	T17	&	IO\_L16P\_T2\_CSI\_B\_14	&	RTM\_FPGA\_LVDS2\_P	\\ \hline
	U17	&	IO\_L16N\_T2\_A15\_D31\_14	&	RTM\_FPGA\_LVDS2\_N	\\ \hline
	T18	&	IO\_L15N\_T2\_DQS\_DOUT\_CSO\_B\_14	&	RTM\_FPGA\_USR\_IO\_N	\\ \hline
	P14	&	IO\_L12P\_T1\_MRCC\_14	&	RTM\_MASTER\_AUX\_CLK\_P	\\ \hline
	R15	&	IO\_L12N\_T1\_MRCC\_14	&	RTM\_MASTER\_AUX\_CLK\_N	\\ \hline

	\end{longtable}
\end{footnotesize}

%---------------------------------------------------------Mez1
\begin{footnotesize}
	\begin{longtable}{|l|p{6cm}|p{6cm}|}
		\hline
		\multicolumn{3}{|c|}{\multirow{2}{*}{\textbf{\large{Mezzanine1 IO}}}}\\
		\multicolumn{3}{|c|}{} \\ \hline 
P1	&	IO\_L9N\_T1\_DQS\_34	&	MEZZ1\_IO0	\\ \hline
M4	&	IO\_L10P\_T1\_34	&	MEZZ1\_IO1	\\ \hline
N4	&	IO\_L10N\_T1\_34	&	MEZZ1\_IO2	\\ \hline
N3	&	IO\_L11P\_T1\_SRCC\_34	&	MEZZ1\_IO3	\\ \hline
N2	&	IO\_L11N\_T1\_SRCC\_34	&	MEZZ1\_IO4	\\ \hline
P4	&	IO\_L12P\_T1\_MRCC\_34	&	MEZZ1\_IO5	\\ \hline
P3	&	IO\_L12N\_T1\_MRCC\_34	&	MEZZ1\_IO6	\\ \hline
R2	&	IO\_L13P\_T2\_MRCC\_34	&	MEZZ1\_IO7	\\ \hline
R1	&	IO\_L13N\_T2\_MRCC\_34	&	MEZZ1\_IO8	\\ \hline
R3	&	IO\_L14P\_T2\_SRCC\_34	&	MEZZ1\_IO9	\\ \hline
T2	&	IO\_L14N\_T2\_SRCC\_34	&	MEZZ1\_IO10	\\ \hline
U2	&	IO\_L15P\_T2\_DQS\_34	&	MEZZ1\_IO11	\\ \hline
U1	&	IO\_L15N\_T2\_DQS\_34	&	MEZZ1\_IO12	\\ \hline
V3	&	IO\_L16P\_T2\_34	&	MEZZ1\_IO13	\\ \hline
V2	&	IO\_L16N\_T2\_34	&	MEZZ1\_IO14	\\ \hline
T4	&	IO\_L17P\_T2\_34	&	MEZZ1\_IO15	\\ \hline
	
	\end{longtable}
\end{footnotesize}

%---------------------------------------------------------mezz2
\begin{footnotesize}
	\begin{longtable}{|l|p{6cm}|p{6cm}|}
		\hline
		\multicolumn{3}{|c|}{\multirow{2}{*}{\textbf{\large{Mezzanine2 IO}}}}\\
		\multicolumn{3}{|c|}{} \\ \hline 
T3	&	IO\_L17N\_T2\_34	&	MEZZ2\_IO0	\\ \hline
U4	&	IO\_L18P\_T2\_34	&	MEZZ2\_IO1	\\ \hline
V4	&	IO\_L18N\_T2\_34	&	MEZZ2\_IO2	\\ \hline
P6	&	IO\_L19P\_T3\_34	&	MEZZ2\_IO3	\\ \hline
P5	&	IO\_L19N\_T3\_VREF\_34	&	MEZZ2\_IO4	\\ \hline
U6	&	IO\_L20P\_T3\_34	&	MEZZ2\_IO5	\\ \hline
U5	&	IO\_L20N\_T3\_34	&	MEZZ2\_IO6	\\ \hline
R5	&	IO\_L21P\_T3\_DQS\_34	&	MEZZ2\_IO7	\\ \hline
T5	&	IO\_L21N\_T3\_DQS\_34	&	MEZZ2\_IO8	\\ \hline
R7	&	IO\_L22P\_T3\_34	&	MEZZ2\_IO9	\\ \hline
T7	&	IO\_L22N\_T3\_34	&	MEZZ2\_IO10	\\ \hline
U7	&	IO\_L23P\_T3\_34	&	MEZZ2\_IO11	\\ \hline
V6	&	IO\_L23N\_T3\_34	&	MEZZ2\_IO12	\\ \hline
V8	&	IO\_L24P\_T3\_34	&	MEZZ2\_IO13	\\ \hline
V7	&	IO\_L24N\_T3\_34	&	MEZZ2\_IO14	\\ \hline
R6	&	IO\_25\_34	&	MEZZ2\_IO15	\\ \hline
	
	\end{longtable}
\end{footnotesize}

%---------------------------------------------------------mezz3
\begin{footnotesize}
	\begin{longtable}{|l|p{6cm}|p{6cm}|}
		\hline
		\multicolumn{3}{|c|}{\multirow{2}{*}{\textbf{\large{Mezzanine3 IO}}}}\\
		\multicolumn{3}{|c|}{} \\ \hline 
D11	&	IO\_L6P\_T0\_15	&	MEZZ3\_IO0	\\ \hline
C12	&	IO\_L6N\_T0\_VREF\_15	&	MEZZ3\_IO1	\\ \hline
B12	&	IO\_L7P\_T1\_AD2P\_15	&	MEZZ3\_IO2	\\ \hline
A12	&	IO\_L7N\_T1\_AD2N\_15	&	MEZZ3\_IO3	\\ \hline
A13	&	IO\_L8P\_T1\_AD10P\_15	&	MEZZ3\_IO4	\\ \hline
A14	&	IO\_L8N\_T1\_AD10N\_15	&	MEZZ3\_IO5	\\ \hline
C14	&	IO\_L9P\_T1\_DQS\_AD3P\_15	&	MEZZ3\_IO6	\\ \hline
B15	&	IO\_L9N\_T1\_DQS\_AD3N\_15	&	MEZZ3\_IO7	\\ \hline
B14	&	IO\_L10P\_T1\_AD11P\_15	&	MEZZ3\_IO8	\\ \hline
A15	&	IO\_L10N\_T1\_AD11N\_15	&	MEZZ3\_IO9	\\ \hline
D13	&	IO\_L11P\_T1\_SRCC\_15	&	MEZZ3\_IO10	\\ \hline
C13	&	IO\_L11N\_T1\_SRCC\_15	&	MEZZ3\_IO11	\\ \hline
E13	&	IO\_L12P\_T1\_MRCC\_15	&	MEZZ3\_IO12	\\ \hline
D14	&	IO\_L12N\_T1\_MRCC\_15	&	MEZZ3\_IO13	\\ \hline
D15	&	IO\_L13N\_T2\_MRCC\_15	&	MEZZ3\_IO14	\\ \hline
E16	&	IO\_L14P\_T2\_SRCC\_15	&	MEZZ3\_IO15	\\ \hline

	\end{longtable}
\end{footnotesize}

%---------------------------------------------------------mezz4
\begin{footnotesize}
	\begin{longtable}{|l|p{6cm}|p{6cm}|}
		\hline
		\multicolumn{3}{|c|}{\multirow{2}{*}{\textbf{\large{Mezzanine4 IO}}}}\\
		\multicolumn{3}{|c|}{} \\ \hline 
K5	&	IO\_L1N\_T0\_34	&	MEZZ4\_IO0	\\ \hline
J5	&	IO\_L2P\_T0\_34	&	MEZZ4\_IO1	\\ \hline
J4	&	IO\_L2N\_T0\_34	&	MEZZ4\_IO2	\\ \hline
K2	&	IO\_L3P\_T0\_DQS\_34	&	MEZZ4\_IO3	\\ \hline
K1	&	IO\_L3N\_T0\_DQS\_34	&	MEZZ4\_IO4	\\ \hline
K3	&	IO\_L4P\_T0\_34	&	MEZZ4\_IO5	\\ \hline
L2	&	IO\_L4N\_T0\_34	&	MEZZ4\_IO6	\\ \hline
L4	&	IO\_L5P\_T0\_34	&	MEZZ4\_IO7	\\ \hline
L3	&	IO\_L5N\_T0\_34	&	MEZZ4\_IO8	\\ \hline
L5	&	IO\_L6P\_T0\_34	&	MEZZ4\_IO9	\\ \hline
M5	&	IO\_L6N\_T0\_VREF\_34	&	MEZZ4\_IO10	\\ \hline
M2	&	IO\_L7P\_T1\_34	&	MEZZ4\_IO11	\\ \hline
M1	&	IO\_L7N\_T1\_34	&	MEZZ4\_IO12	\\ \hline
M6	&	IO\_L8P\_T1\_34	&	MEZZ4\_IO13	\\ \hline
N6	&	IO\_L8N\_T1\_34	&	MEZZ4\_IO14	\\ \hline
N1	&	IO\_L9P\_T1\_DQS\_34	&	MEZZ4\_IO15	\\ \hline

	\end{longtable}
\end{footnotesize}

%---------------------------------------------------------clk
\begin{footnotesize}
	\begin{longtable}{|l|p{6cm}|p{6cm}|}
		\hline
		\multicolumn{3}{|c|}{\multirow{2}{*}{\textbf{\large{Mezzanine CLK IO}}}}\\
		\multicolumn{3}{|c|}{} \\ \hline 
D18	&	IO\_L17N\_T2\_A25\_15	&	CLK\_MEZZ\_IO0	\\ \hline
C17	&	IO\_L18P\_T2\_A24\_15	&	CLK\_MEZZ\_IO1	\\ \hline
C18	&	IO\_L18N\_T2\_A23\_15	&	CLK\_MEZZ\_IO2	\\ \hline
G17	&	IO\_L19P\_T3\_A22\_15	&	CLK\_MEZZ\_IO3	\\ \hline
F18	&	IO\_L19N\_T3\_A21\_VREF\_15	&	CLK\_MEZZ\_IO4	\\ \hline
H16	&	IO\_L20P\_T3\_A20\_15	&	CLK\_MEZZ\_IO5	\\ \hline
G16	&	IO\_L20N\_T3\_A19\_15	&	CLK\_MEZZ\_IO6	\\ \hline
G15	&	IO\_L21P\_T3\_DQS\_15	&	CLK\_MEZZ\_IO7	\\ \hline
F15	&	IO\_L21N\_T3\_DQS\_A18\_15	&	CLK\_MEZZ\_IO8	\\ \hline
G14	&	IO\_L22P\_T3\_A17\_15	&	CLK\_MEZZ\_IO9	\\ \hline
F14	&	IO\_L22N\_T3\_A16\_15	&	CLK\_MEZZ\_IO10	\\ \hline
H17	&	IO\_L23P\_T3\_FOE\_B\_15	&	CLK\_MEZZ\_IO11	\\ \hline
H18	&	IO\_L23N\_T3\_FWE\_B\_15	&	CLK\_MEZZ\_IO12	\\ \hline
F17	&	IO\_L24P\_T3\_RS1\_15	&	CLK\_MEZZ\_IO13	\\ \hline
H14	&	IO\_25\_15	&	CLK\_MEZZ\_IO14	\\ \hline
&	IO\_L24N\_T3\_RS0\_15	&	CLK\_MEZZ\_IO15	\\ \hline

	\end{longtable}
\end{footnotesize}

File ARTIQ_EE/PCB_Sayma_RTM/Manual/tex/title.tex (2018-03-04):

\begin{titlepage}

\textcolor{white}{xxx} 
\vskip 1 true in

\begin{wrapfigure}{l}{0.01\textwidth}
	\begin{center}
		\vspace{-35pt}
		
	\end{center}
\end{wrapfigure}

\textbf{{\LARGE \nazwa}} \\
\linebreak
\textbf{ {\indent \indent \LARGE specification}}\\
\vskip 0.8 true in

\begin{figure}[htbp!]
	\centering
	\\
	%	\caption{v3.1(02.2017)}
\end{figure}
\begin{center}
	v1.0(02.2018)
\end{center}

\vskip 0.7 true in

\end{titlepage}

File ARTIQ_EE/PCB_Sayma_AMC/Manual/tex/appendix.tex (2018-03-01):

\section{Total table of sugnals}

\begin{footnotesize}
	\begin{longtable}{|p{7cm}|p{1cm}|p{5cm}|}
		\hline
%		\multicolumn{3}{|c|}{\multirow{2}{*}{\textbf{\large{Table 12 - FMC }}}} \\
FPGA signal	&	FPGA ball	&	Signal on the board	\\ \hline
CCLK\_0	&	AA9	&	FPGA\_CCLK	\\ \hline
CFGBVS\_0	&	W7	&	P3V3	\\ \hline
D00\_MOSI\_0	&	AC7	&	QSPI0\_IO0	\\ \hline
D01\_DIN\_0	&	AB7	&	QSPI0\_IO1	\\ \hline
D02\_0	&	AA7	&	QSPI0\_IO2	\\ \hline
D03\_0	&	Y7	&	QSPI0\_IO3	\\ \hline
DONE\_0	&	N7	&	FPGA\_DONE	\\ \hline
DXN	&	Y11	&	DXN	\\ \hline
DXP	&	Y12	&	DXP	\\ \hline
GND-1	&	A2	&	GND	\\ \hline
GND-1	&	T20	&	GND	\\ \hline
GND-10	&	A32	&	GND	\\ \hline
GND-10	&	U5	&	GND	\\ \hline
GND-100	&	AJ1	&	GND	\\ \hline
GND-100	&	N9	&	GND	\\ \hline
GND-101	&	AJ2	&	GND	\\ \hline
GND-101	&	N11	&	GND	\\ \hline
GND-102	&	AJ5	&	GND	\\ \hline
GND-102	&	N13	&	GND	\\ \hline
GND-103	&	AJ7	&	GND	\\ \hline
GND-103	&	N15	&	GND	\\ \hline
GND-104	&	AJ17	&	GND	\\ \hline
GND-104	&	N17	&	GND	\\ \hline
GND-105	&	AJ27	&	GND	\\ \hline
GND-105	&	N19	&	GND	\\ \hline
GND-106	&	AK3	&	GND	\\ \hline
GND-106	&	N25	&	GND	\\ \hline
GND-107	&	AK4	&	GND	\\ \hline
GND-107	&	N28	&	GND	\\ \hline
GND-108	&	AK7	&	GND	\\ \hline
GND-108	&	N32	&	GND	\\ \hline
GND-109	&	AK14	&	GND	\\ \hline
GND-109	&	P3	&	GND	\\ \hline
GND-11	&	B3	&	GND	\\ \hline
GND-11	&	Y8	&	GND	\\ \hline
GND-110	&	AK24	&	GND	\\ \hline
GND-110	&	P4	&	GND	\\ \hline
GND-111	&	AK34	&	GND	\\ \hline
GND-111	&	P10	&	GND	\\ \hline
GND-112	&	AL1	&	GND	\\ \hline
GND-112	&	P12	&	GND	\\ \hline
GND-113	&	AL5	&	GND	\\ \hline
GND-113	&	P14	&	GND	\\ \hline
GND-114	&	AL7	&	GND	\\ \hline
GND-114	&	P16	&	GND	\\ \hline
GND-115	&	AL11	&	GND	\\ \hline
GND-115	&	P18	&	GND	\\ \hline
GND-116	&	AL21	&	GND	\\ \hline
GND-116	&	P22	&	GND	\\ \hline
GND-117	&	AL31	&	GND	\\ \hline
GND-117	&	P28	&	GND	\\ \hline
GND-118	&	AM4	&	GND	\\ \hline
GND-118	&	P30	&	GND	\\ \hline
GND-119	&	AM7	&	GND	\\ \hline
GND-119	&	P34	&	GND	\\ \hline
GND-12	&	B4	&	GND	\\ \hline
GND-12	&	U13	&	GND	\\ \hline
GND-120	&	AM8	&	GND	\\ \hline
GND-120	&	R1	&	GND	\\ \hline
GND-121	&	AM18	&	GND	\\ \hline
GND-121	&	R5	&	GND	\\ \hline
GND-122	&	AM28	&	GND	\\ \hline
GND-122	&	R9	&	GND	\\ \hline
GND-123	&	AN1	&	GND	\\ \hline
GND-123	&	R11	&	GND	\\ \hline
GND-124	&	AN2	&	GND	\\ \hline
GND-124	&	R13	&	GND	\\ \hline
GND-125	&	AN5	&	GND	\\ \hline
GND-125	&	R15	&	GND	\\ \hline
GND-126	&	AN7	&	GND	\\ \hline
GND-126	&	R17	&	GND	\\ \hline
GND-127	&	AN15	&	GND	\\ \hline
GND-127	&	R19	&	GND	\\ \hline
GND-128	&	AN25	&	GND	\\ \hline
GND-128	&	R28	&	GND	\\ \hline
GND-129	&	AP3	&	GND	\\ \hline
GND-129	&	R31	&	GND	\\ \hline
GND-13	&	B7	&	GND	\\ \hline
GND-13	&	U15	&	GND	\\ \hline
GND-130	&	AP4	&	GND	\\ \hline
GND-130	&	T4	&	GND	\\ \hline
GND-131	&	AP7	&	GND	\\ \hline
GND-131	&	T8	&	GND	\\ \hline
GND-132	&	AP12	&	GND	\\ \hline
GND-132	&	T10	&	GND	\\ \hline
GND-133	&	AP22	&	GND	\\ \hline
GND-133	&	T12	&	GND	\\ \hline
GND-134	&	AP32	&	GND	\\ \hline
GND-134	&	T14	&	GND	\\ \hline
GND-135	&	T16	&	GND	\\ \hline
GND-136	&	T18	&	GND	\\ \hline
GND-14	&	B8	&	GND	\\ \hline
GND-14	&	U17	&	GND	\\ \hline
GND-15	&	B18	&	GND	\\ \hline
GND-15	&	U19	&	GND	\\ \hline
GND-16	&	B28	&	GND	\\ \hline
GND-16	&	U23	&	GND	\\ \hline
GND-17	&	B30	&	GND	\\ \hline
GND-17	&	U30	&	GND	\\ \hline
GND-18	&	B33	&	GND	\\ \hline
GND-18	&	U31	&	GND	\\ \hline
GND-19	&	B34	&	GND	\\ \hline
GND-19	&	U32	&	GND	\\ \hline
GND-2	&	A1	&	GND	\\ \hline
GND-2	&	T26	&	GND	\\ \hline
GND-20	&	C1	&	GND	\\ \hline
GND-20	&	U33	&	GND	\\ \hline
GND-21	&	C5	&	GND	\\ \hline
GND-21	&	V3	&	GND	\\ \hline
GND-22	&	C7	&	GND	\\ \hline
GND-22	&	V4	&	GND	\\ \hline
GND-23	&	C15	&	GND	\\ \hline
GND-23	&	V10	&	GND	\\ \hline
GND-24	&	C25	&	GND	\\ \hline
GND-24	&	V14	&	GND	\\ \hline
GND-25	&	C30	&	GND	\\ \hline
GND-25	&	V16	&	GND	\\ \hline
GND-26	&	C31	&	GND	\\ \hline
GND-26	&	V18	&	GND	\\ \hline
GND-27	&	D4	&	GND	\\ \hline
GND-27	&	V20	&	GND	\\ \hline
GND-28	&	D7	&	GND	\\ \hline
GND-28	&	V30	&	GND	\\ \hline
GND-29	&	D12	&	GND	\\ \hline
GND-29	&	W1	&	GND	\\ \hline
GND-3	&	A5	&	GND	\\ \hline
GND-3	&	T28	&	GND	\\ \hline
GND-30	&	D22	&	GND	\\ \hline
GND-30	&	W5	&	GND	\\ \hline
GND-31	&	AB8	&	GND	\\ \hline
GND-31	&	D30	&	GND	\\ \hline
GND-32	&	D34	&	GND	\\ \hline
GND-32	&	W13	&	GND	\\ \hline
GND-33	&	E1	&	GND	\\ \hline
GND-33	&	W15	&	GND	\\ \hline
GND-34	&	E2	&	GND	\\ \hline
GND-34	&	W17	&	GND	\\ \hline
GND-35	&	E5	&	GND	\\ \hline
GND-35	&	W19	&	GND	\\ \hline
GND-36	&	E7	&	GND	\\ \hline
GND-36	&	W27	&	GND	\\ \hline
GND-37	&	E9	&	GND	\\ \hline
GND-37	&	Y4	&	GND	\\ \hline
GND-38	&	E19	&	GND	\\ \hline
GND-38	&	Y10	&	GND	\\ \hline
GND-39	&	E29	&	GND	\\ \hline
GND-39	&	Y14	&	GND	\\ \hline
GND-4	&	A6	&	GND	\\ \hline
GND-4	&	T29	&	GND	\\ \hline
GND-40	&	E30	&	GND	\\ \hline
GND-40	&	Y16	&	GND	\\ \hline
GND-41	&	E32	&	GND	\\ \hline
GND-41	&	Y18	&	GND	\\ \hline
GND-42	&	F3	&	GND	\\ \hline
GND-42	&	Y20	&	GND	\\ \hline
GND-43	&	F4	&	GND	\\ \hline
GND-43	&	Y24	&	GND	\\ \hline
GND-44	&	F7	&	GND	\\ \hline
GND-44	&	Y34	&	GND	\\ \hline
GND-45	&	AA1	&	GND	\\ \hline
GND-45	&	F16	&	GND	\\ \hline
GND-46	&	AA2	&	GND	\\ \hline
GND-46	&	F26	&	GND	\\ \hline
GND-47	&	AA5	&	GND	\\ \hline
GND-47	&	F28	&	GND	\\ \hline
GND-48	&	F29	&	GND	\\ \hline
GND-48	&	P8	&	GND	\\ \hline
GND-49	&	AA11	&	GND	\\ \hline
GND-49	&	F33	&	GND	\\ \hline
GND-5	&	A7	&	GND	\\ \hline
GND-5	&	T30	&	GND	\\ \hline
GND-50	&	AA13	&	GND	\\ \hline
GND-50	&	F34	&	GND	\\ \hline
GND-51	&	AA15	&	GND	\\ \hline
GND-51	&	G1	&	GND	\\ \hline
GND-52	&	AA17	&	GND	\\ \hline
GND-52	&	G5	&	GND	\\ \hline
GND-53	&	AA19	&	GND	\\ \hline
GND-53	&	G7	&	GND	\\ \hline
GND-54	&	AA21	&	GND	\\ \hline
GND-54	&	G13	&	GND	\\ \hline
GND-55	&	AA31	&	GND	\\ \hline
GND-55	&	G23	&	GND	\\ \hline
GND-56	&	AB3	&	GND	\\ \hline
GND-56	&	G28	&	GND	\\ \hline
GND-57	&	AB4	&	GND	\\ \hline
GND-57	&	G31	&	GND	\\ \hline
GND-58	&	AB10	&	GND	\\ \hline
GND-58	&	H4	&	GND	\\ \hline
GND-59	&	AB12	&	GND	\\ \hline
GND-59	&	H7	&	GND	\\ \hline
GND-6	&	A11	&	GND	\\ \hline
GND-6	&	T33	&	GND	\\ \hline
GND-60	&	AB14	&	GND	\\ \hline
GND-60	&	H10	&	GND	\\ \hline
GND-61	&	AB16	&	GND	\\ \hline
GND-61	&	H20	&	GND	\\ \hline
GND-62	&	AB18	&	GND	\\ \hline
GND-62	&	H28	&	GND	\\ \hline
GND-63	&	AB28	&	GND	\\ \hline
GND-63	&	H30	&	GND	\\ \hline
GND-64	&	AC1	&	GND	\\ \hline
GND-64	&	H34	&	GND	\\ \hline
GND-65	&	AC5	&	GND	\\ \hline
GND-65	&	J1	&	GND	\\ \hline
GND-66	&	J2	&	GND	\\ \hline
GND-66	&	V8	&	GND	\\ \hline
GND-67	&	AC11	&	GND	\\ \hline
GND-67	&	J5	&	GND	\\ \hline
GND-68	&	AC13	&	GND	\\ \hline
GND-68	&	J7	&	GND	\\ \hline
GND-69	&	AC15	&	GND	\\ \hline
GND-69	&	J17	&	GND	\\ \hline
GND-7	&	A21	&	GND	\\ \hline
GND-7	&	T34	&	GND	\\ \hline
GND-70	&	AC17	&	GND	\\ \hline
GND-70	&	J27	&	GND	\\ \hline
GND-71	&	AC19	&	GND	\\ \hline
GND-71	&	J28	&	GND	\\ \hline
GND-72	&	AC25	&	GND	\\ \hline
GND-72	&	J32	&	GND	\\ \hline
GND-73	&	AD4	&	GND	\\ \hline
GND-73	&	K3	&	GND	\\ \hline
GND-74	&	AD12	&	GND	\\ \hline
GND-74	&	K4	&	GND	\\ \hline
GND-75	&	AD22	&	GND	\\ \hline
GND-75	&	K14	&	GND	\\ \hline
GND-76	&	AD32	&	GND	\\ \hline
GND-76	&	K24	&	GND	\\ \hline
GND-77	&	AE1	&	GND	\\ \hline
GND-77	&	K28	&	GND	\\ \hline
GND-78	&	AE2	&	GND	\\ \hline
GND-78	&	K30	&	GND	\\ \hline
GND-79	&	AE5	&	GND	\\ \hline
GND-79	&	K34	&	GND	\\ \hline
GND-8	&	A30	&	GND	\\ \hline
GND-8	&	U1	&	GND	\\ \hline
GND-80	&	AE7	&	GND	\\ \hline
GND-80	&	L1	&	GND	\\ \hline
GND-81	&	AE9	&	GND	\\ \hline
GND-81	&	L5	&	GND	\\ \hline
GND-82	&	AE19	&	GND	\\ \hline
GND-82	&	L11	&	GND	\\ \hline
GND-83	&	AE29	&	GND	\\ \hline
GND-83	&	L21	&	GND	\\ \hline
GND-84	&	AF3	&	GND	\\ \hline
GND-84	&	L28	&	GND	\\ \hline
GND-85	&	AF4	&	GND	\\ \hline
GND-85	&	L31	&	GND	\\ \hline
GND-86	&	AF7	&	GND	\\ \hline
GND-86	&	M4	&	GND	\\ \hline
GND-87	&	AF16	&	GND	\\ \hline
GND-87	&	M8	&	GND	\\ \hline
GND-88	&	AF26	&	GND	\\ \hline
GND-88	&	M10	&	GND	\\ \hline
GND-89	&	AG1	&	GND	\\ \hline
GND-89	&	M12	&	GND	\\ \hline
GND-9	&	A31	&	GND	\\ \hline
GND-9	&	U2	&	GND	\\ \hline
GND-90	&	AG5	&	GND	\\ \hline
GND-90	&	M14	&	GND	\\ \hline
GND-91	&	AG7	&	GND	\\ \hline
GND-91	&	M16	&	GND	\\ \hline
GND-92	&	AG13	&	GND	\\ \hline
GND-92	&	M18	&	GND	\\ \hline
GND-93	&	AG23	&	GND	\\ \hline
GND-93	&	M28	&	GND	\\ \hline
GND-94	&	AG33	&	GND	\\ \hline
GND-94	&	M30	&	GND	\\ \hline
GND-95	&	AH4	&	GND	\\ \hline
GND-95	&	M33	&	GND	\\ \hline
GND-96	&	AH7	&	GND	\\ \hline
GND-96	&	M34	&	GND	\\ \hline
GND-97	&	AH10	&	GND	\\ \hline
GND-97	&	N1	&	GND	\\ \hline
GND-98	&	AH20	&	GND	\\ \hline
GND-98	&	N2	&	GND	\\ \hline
GND-99	&	AH30	&	GND	\\ \hline
GND-99	&	N5	&	GND	\\ \hline
GNDADC	&	U11	&	GND	\\ \hline
INIT\_B\_0	&	V7	&	FPGA\_INIT\_B	\\ \hline
IO\_L10N\_T1U\_N7\_QBC\_AD4N\_44	&	AJ25	&	DDR3\_64\_DQS1\_N	\\ \hline
IO\_L10N\_T1U\_N7\_QBC\_AD4N\_45	&	AL17	&	DDR3\_64\_A1	\\ \hline
IO\_L10N\_T1U\_N7\_QBC\_AD4N\_46	&	AP30	&	DDR3\_64\_DQS5\_N	\\ \hline
IO\_L10N\_T1U\_N7\_QBC\_AD4N\_47	&	AC21	&	FMC1\_LA23\_N	\\ \hline
IO\_L10N\_T1U\_N7\_QBC\_AD4N\_48	&	AF34	&	FMC1\_LA05\_N	\\ \hline
IO\_L10N\_T1U\_N7\_QBC\_AD4N\_64	&	AE11	&	DIO6	\\ \hline
IO\_L10N\_T1U\_N7\_QBC\_AD4N\_66	&	J10	&	SYNCOUT21\_N	\\ \hline
IO\_L10N\_T1U\_N7\_QBC\_AD4N\_67	&	A24	&	DDR3\_32\_DQS1\_N	\\ \hline
IO\_L10N\_T1U\_N7\_QBC\_AD4N\_68	&	D18	&	DDR3\_32\_A10	\\ \hline
IO\_L10N\_T1U\_N7\_QBC\_AD4N\_A13\_D29\_65	&	K23	&	SMA\_IO1	\\ \hline
IO\_L10P\_T1U\_N6\_QBC\_AD4P\_44	&	AH24	&	DDR3\_64\_DQS1\_P	\\ \hline
IO\_L10P\_T1U\_N6\_QBC\_AD4P\_45	&	AL18	&	DDR3\_64\_A10	\\ \hline
IO\_L10P\_T1U\_N6\_QBC\_AD4P\_46	&	AN29	&	DDR3\_64\_DQS5\_P	\\ \hline
IO\_L10P\_T1U\_N6\_QBC\_AD4P\_47	&	AB21	&	FMC1\_LA23\_P	\\ \hline
IO\_L10P\_T1U\_N6\_QBC\_AD4P\_48	&	AE33	&	FMC1\_LA05\_P	\\ \hline
IO\_L10P\_T1U\_N6\_QBC\_AD4P\_64	&	AD11	&	DIO5	\\ \hline
IO\_L10P\_T1U\_N6\_QBC\_AD4P\_66	&	K10	&	SYNCOUT21\_P	\\ \hline
IO\_L10P\_T1U\_N6\_QBC\_AD4P\_67	&	B24	&	DDR3\_32\_DQS1\_P	\\ \hline
IO\_L10P\_T1U\_N6\_QBC\_AD4P\_68	&	D19	&	NC	\\ \hline
IO\_L10P\_T1U\_N6\_QBC\_AD4P\_A12\_D28\_65	&	L22	&	SI5324\_INT\_ALM	\\ \hline
IO\_L11N\_T1U\_N9\_GC\_44	&	AJ24	&	DDR3\_64\_DQ8	\\ \hline
IO\_L11N\_T1U\_N9\_GC\_45	&	AK18	&	DDR3\_64\_CAS\_N	\\ \hline
IO\_L11N\_T1U\_N9\_GC\_46	&	AM29	&	DDR3\_64\_DQ46	\\ \hline
IO\_L11N\_T1U\_N9\_GC\_47	&	AA23	&	FMC1\_CLK1\_M2C\_N	\\ \hline
IO\_L11N\_T1U\_N9\_GC\_48	&	AD31	&	FMC1\_LA08\_N	\\ \hline
IO\_L11N\_T1U\_N9\_GC\_64	&	AH12	&	DIO4	\\ \hline
IO\_L11N\_T1U\_N9\_GC\_66	&	F9	&	ADC1\_SYNC\_N	\\ \hline
IO\_L11N\_T1U\_N9\_GC\_67	&	D25	&	DDR3\_32\_DQ8	\\ \hline
IO\_L11N\_T1U\_N9\_GC\_68	&	D16	&	DDR3\_32\_WE\_N	\\ \hline
IO\_L11N\_T1U\_N9\_GC\_A11\_D27\_65	&	M26	&	TCKC\_D\_N	\\ \hline
IO\_L11P\_T1U\_N8\_GC\_44	&	AJ23	&	DDR3\_64\_DQ10	\\ \hline
IO\_L11P\_T1U\_N8\_GC\_45	&	AJ18	&	DDR3\_64\_ODT	\\ \hline
IO\_L11P\_T1U\_N8\_GC\_46	&	AL29	&	DDR3\_64\_DQ44	\\ \hline
IO\_L11P\_T1U\_N8\_GC\_47	&	Y23	&	FMC1\_CLK1\_M2C\_P	\\ \hline
IO\_L11P\_T1U\_N8\_GC\_48	&	AD30	&	FMC1\_LA08\_P	\\ \hline
IO\_L11P\_T1U\_N8\_GC\_64	&	AG12	&	DIO3	\\ \hline
IO\_L11P\_T1U\_N8\_GC\_66	&	G9	&	ADC1\_SYNC\_P	\\ \hline
IO\_L11P\_T1U\_N8\_GC\_67	&	E25	&	DDR3\_32\_DQ10	\\ \hline
IO\_L11P\_T1U\_N8\_GC\_68	&	E16	&	DDR3\_32\_CAS\_N	\\ \hline
IO\_L11P\_T1U\_N8\_GC\_A10\_D26\_65	&	M25	&	TCKC\_D\_P	\\ \hline
IO\_L12N\_T1U\_N11\_GC\_44	&	AH23	&	DDR3\_64\_DQ12	\\ \hline
IO\_L12N\_T1U\_N11\_GC\_45	&	AK16	&	SYSCLK\_300\_N	\\ \hline
IO\_L12N\_T1U\_N11\_GC\_46	&	AM30	&	DDR3\_64\_DQ42	\\ \hline
IO\_L12N\_T1U\_N11\_GC\_47	&	AA25	&	FMC1\_CLK0\_M2C\_N	\\ \hline
IO\_L12N\_T1U\_N11\_GC\_48	&	AC32	&	FMC1\_GBTCLK0\_M2C\_N	\\ \hline
IO\_L12N\_T1U\_N11\_GC\_64	&	AH11	&	DIO1	\\ \hline
IO\_L12N\_T1U\_N11\_GC\_66	&	F10	&	NC	\\ \hline
IO\_L12N\_T1U\_N11\_GC\_67	&	C24	&	DDR3\_32\_DQ12	\\ \hline
IO\_L12N\_T1U\_N11\_GC\_68	&	E17	&	NC	\\ \hline
IO\_L12N\_T1U\_N11\_GC\_A09\_D25\_65	&	M24	&	TCKC\_C\_N	\\ \hline
IO\_L12P\_T1U\_N10\_GC\_44	&	AH22	&	DDR3\_64\_DQ14	\\ \hline
IO\_L12P\_T1U\_N10\_GC\_45	&	AK17	&	SYSCLK\_300\_P	\\ \hline
IO\_L12P\_T1U\_N10\_GC\_46	&	AL30	&	DDR3\_64\_DQ40	\\ \hline
IO\_L12P\_T1U\_N10\_GC\_47	&	AA24	&	FMC1\_CLK0\_M2C\_P	\\ \hline
IO\_L12P\_T1U\_N10\_GC\_48	&	AC31	&	FMC1\_GBTCLK0\_M2C\_P	\\ \hline
IO\_L12P\_T1U\_N10\_GC\_64	&	AG11	&	DIO0	\\ \hline
IO\_L12P\_T1U\_N10\_GC\_66	&	G10	&	NC	\\ \hline
IO\_L12P\_T1U\_N10\_GC\_67	&	D24	&	DDR3\_32\_DQ14	\\ \hline
IO\_L12P\_T1U\_N10\_GC\_68	&	E18	&	DDR3\_32\_RAS\_N	\\ \hline
IO\_L12P\_T1U\_N10\_GC\_A08\_D24\_65	&	N24	&	TCKC\_C\_P	\\ \hline
IO\_L13N\_T2L\_N1\_GC\_QBC\_44	&	AK21	&	HW\_ID3	\\ \hline
IO\_L13N\_T2L\_N1\_GC\_QBC\_45	&	AH17	&	TXC6\_N	\\ \hline
IO\_L13N\_T2L\_N1\_GC\_QBC\_46	&	AK30	&	NC	\\ \hline
IO\_L13N\_T2L\_N1\_GC\_QBC\_47	&	W24	&	FMC1\_LA17\_CC\_N	\\ \hline
IO\_L13N\_T2L\_N1\_GC\_QBC\_48	&	AB32	&	FMC1\_LA00\_CC\_N	\\ \hline
IO\_L13N\_T2L\_N1\_GC\_QBC\_64	&	AG10	&	AMC\_MASTER\_AUX\_CLK\_N	\\ \hline
IO\_L13N\_T2L\_N1\_GC\_QBC\_66	&	G11	&	SYNCOUT11\_N	\\ \hline
IO\_L13N\_T2L\_N1\_GC\_QBC\_67	&	C23	&	NC	\\ \hline
IO\_L13N\_T2L\_N1\_GC\_QBC\_68	&	G16	&	DDR3\_32\_BA2	\\ \hline
IO\_L13N\_T2L\_N1\_GC\_QBC\_A07\_D23\_65	&	N26	&	TCKC\_B\_N	\\ \hline
IO\_L13P\_T2L\_N0\_GC\_QBC\_44	&	AJ21	&	DDR3\_64\_DM2	\\ \hline
IO\_L13P\_T2L\_N0\_GC\_QBC\_45	&	AH18	&	TXC6\_P	\\ \hline
IO\_L13P\_T2L\_N0\_GC\_QBC\_46	&	AJ29	&	DDR3\_64\_DM6	\\ \hline
IO\_L13P\_T2L\_N0\_GC\_QBC\_47	&	W23	&	FMC1\_LA17\_CC\_P	\\ \hline
IO\_L13P\_T2L\_N0\_GC\_QBC\_48	&	AA32	&	FMC1\_LA00\_CC\_P	\\ \hline
IO\_L13P\_T2L\_N0\_GC\_QBC\_64	&	AF10	&	AMC\_MASTER\_AUX\_CLK\_P	\\ \hline
IO\_L13P\_T2L\_N0\_GC\_QBC\_66	&	H11	&	SYNCOUT11\_P	\\ \hline
IO\_L13P\_T2L\_N0\_GC\_QBC\_67	&	D23	&	DDR3\_32\_DM2	\\ \hline
IO\_L13P\_T2L\_N0\_GC\_QBC\_68	&	G17	&	NC	\\ \hline
IO\_L13P\_T2L\_N0\_GC\_QBC\_A06\_D22\_65	&	P26	&	TCKC\_B\_P	\\ \hline
IO\_L14N\_T2L\_N3\_GC\_44	&	AK23	&	DDR3\_64\_DQ19	\\ \hline
IO\_L14N\_T2L\_N3\_GC\_45	&	AJ16	&	RXC6\_N	\\ \hline
IO\_L14N\_T2L\_N3\_GC\_46	&	AK32	&	DDR3\_64\_DQ55	\\ \hline
IO\_L14N\_T2L\_N3\_GC\_47	&	Y25	&	FMC1\_LA18\_CC\_N	\\ \hline
IO\_L14N\_T2L\_N3\_GC\_48	&	AB31	&	FMC1\_LA01\_CC\_N	\\ \hline
IO\_L14N\_T2L\_N3\_GC\_64	&	AG9	&	SFP1\_LED1	\\ \hline
IO\_L14N\_T2L\_N3\_GC\_66	&	G12	&	CDR\_CLK\_CLEAN1\_N	\\ \hline
IO\_L14N\_T2L\_N3\_GC\_67	&	E23	&	DDR3\_32\_DQ19	\\ \hline
IO\_L14N\_T2L\_N3\_GC\_68	&	F17	&	SYSCLK1\_300\_N	\\ \hline
IO\_L14N\_T2L\_N3\_GC\_A05\_D21\_65	&	P25	&	TCKC\_A\_N	\\ \hline
IO\_L14P\_T2L\_N2\_GC\_44	&	AK22	&	DDR3\_64\_DQ20	\\ \hline
IO\_L14P\_T2L\_N2\_GC\_45	&	AH16	&	RXC6\_P	\\ \hline
IO\_L14P\_T2L\_N2\_GC\_46	&	AK31	&	DDR3\_64\_DQ51	\\ \hline
IO\_L14P\_T2L\_N2\_GC\_47	&	W25	&	FMC1\_LA18\_CC\_P	\\ \hline
IO\_L14P\_T2L\_N2\_GC\_48	&	AB30	&	FMC1\_LA01\_CC\_P	\\ \hline
IO\_L14P\_T2L\_N2\_GC\_64	&	AF9	&	CLK\_50M	\\ \hline
IO\_L14P\_T2L\_N2\_GC\_66	&	H12	&	CDR\_CLK\_CLEAN1\_P	\\ \hline
IO\_L14P\_T2L\_N2\_GC\_67	&	E22	&	DDR3\_32\_DQ20	\\ \hline
IO\_L14P\_T2L\_N2\_GC\_68	&	F18	&	SYSCLK1\_300\_P	\\ \hline
IO\_L14P\_T2L\_N2\_GC\_A04\_D20\_65	&	P24	&	TCKC\_A\_P	\\ \hline
IO\_L15N\_T2L\_N5\_AD11N\_44	&	AM20	&	DDR3\_64\_DQ18	\\ \hline
IO\_L15N\_T2L\_N5\_AD11N\_45	&	AG16	&	DDR3\_64\_A2	\\ \hline
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

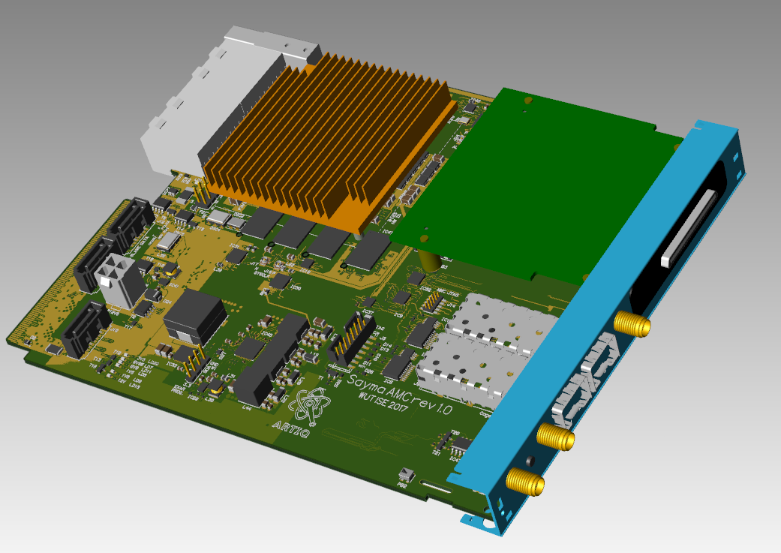
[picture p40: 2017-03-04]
ARTIQ_EE/PCB_Sayma_AMC/Manual/img/front.png

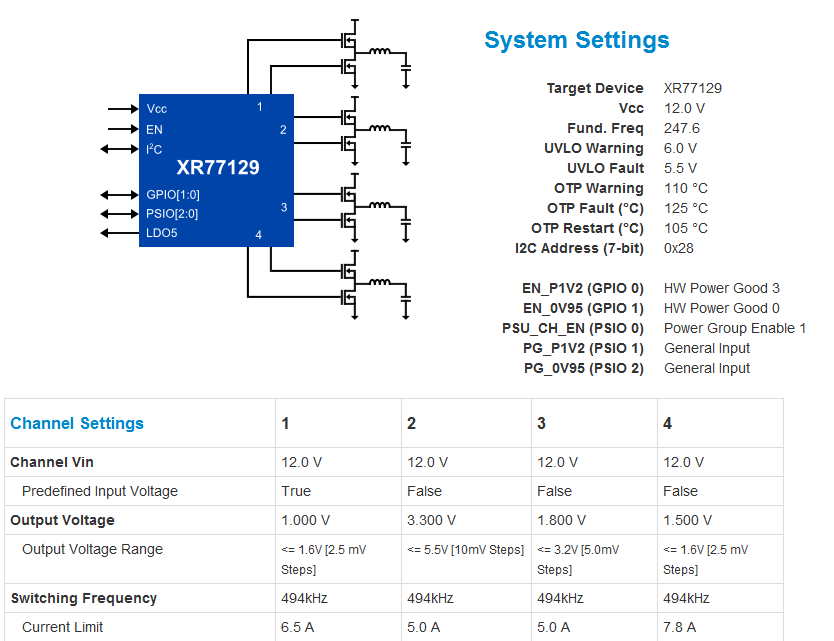
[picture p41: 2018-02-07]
ARTIQ_EE/PCB_Sayma_RTM/Manual/img/exarconf.png

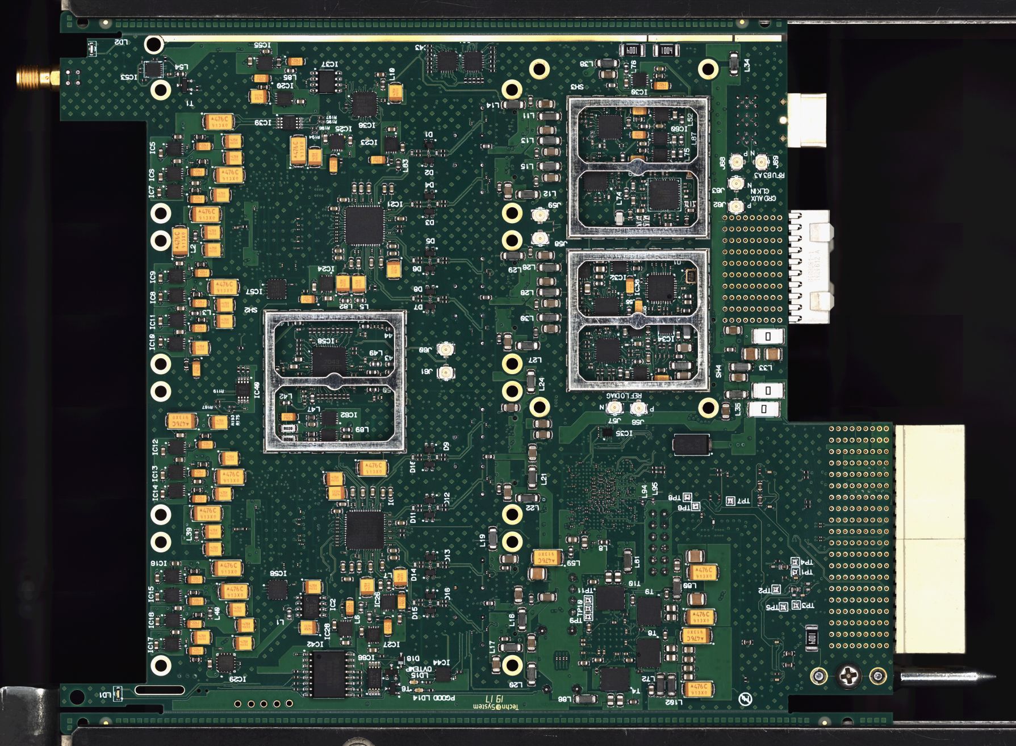
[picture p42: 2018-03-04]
ARTIQ_EE/PCB_Sayma_RTM/Manual/img/bot.jpg

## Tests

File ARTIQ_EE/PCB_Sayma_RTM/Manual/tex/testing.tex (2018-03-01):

\section{Factory acceptance testing}

TBD

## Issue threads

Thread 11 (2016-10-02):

sinara-hw/sinara #11: thermal design

sbourdeauducq, 2016-10-02:
Do the DACs need to be actively cooled or even temperature-stabilized? If so, how?

gkasprow, 2016-10-02:
We had a discussion in Warsaw about it.
Certainly the DACs will be cooled by MTCA fans and some crate-wide temperature regulation is possible.
The idea is to place additional 24bit ADC connected to the DAC (or mezzanine) outputs so on-line compensation will be performed. We will compensate for gain and offset changes.
The ADC will be connected to dedicated pins of mezzanine connector so the DAC driver offset can be compensated as well.
We will use  AD7194 for this purpose with external ppm reference.

jbqubit, 2016-10-04:
I think it's reasonable to assume temperature of air supplied to microTCA chassis is stable to +/- 2 C. 

Also from discussion in Warsaw... I'll close #13. 
- [ ] is it possible to achieve 1 LSB stability for both ADC and DAC? 
    - [ ] is 1 LSB accuracy needed board-to-board? 
- [ ] regarding on-board DC calibration
    - use heavy low-pass; sigma-delta DAC on motherboard, 16 single-ended inputs
    - SPI interface
    - [ ] how many channels are needed? (temperature, voltage measurements)
    - [ ]  allocate several pins (how many?) on 40-pin header #40 for routing to calibration ADC @gkasprow 
- [ ] analog component temperature coefficients (DACs, ADCs, amplifiers, attenuators) 
- [ ] are voltage references needed? 
- [ ] power supply noise rejection of components -- should this go on another Issue?

jordens, 2016-10-04:
@jbqubit please don't be sloppy and keep the top comment up to date. Move text if necessary.

jbqubit, 2016-10-04:
OK. I didn't know that was OK. Edited, improved.

-------
Joe Britton
Sensors and Electron Devices
Army Research Lab
2800 Powder Mill Rd
Adelphi, MD 20783
301-394-3130
joseph.w.britton5.civ@mail.mil

jordens, 2016-10-07:
@jbqubit @gkasprow could you then mark those tasks as done or reraise them where approriate?
Also, who should resolve/answer the tasks that need handling?

dhslichter, 2016-10-10:
Temperature monitoring can also be performed on mezzanines by using [ADT7420](http://www.analog.com/en/products/analog-to-digital-converters/integrated-special-purpose-converters/integrated-temperature-sensors/adt7420.html), which contains conversion and I2C hardware, thus freeing slow ADC lines for e.g. monitoring of I/Q modulator drift or amplifier gain drift.

closed 2017-02-16 by jbqubit

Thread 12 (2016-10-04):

sinara-hw/sinara #12: analog mezzanine power and IO

jbqubit, 2016-10-04:
In #8 Greg recommends 40 pin headers.

>For digital IO and control I'd like to use Samtec hermaphroditic, 
>40 pins connectors: LSS-120-01-L-DV-A and LSS-120-02-L-DV-A 
>which combined give exactly 9mm. I use them in other projects 
>and they work well with frequent mating.

From discussion in Warsaw.... 
- digital signal lines
    - pins [1,...,16] are digital I/O
    - if daughter uses SPI
    - pins [1, 2, 3, 4,...,16] are [SCLK, MOSI, MISO, CS0,...,CSn], 50 MHz maximum
    - all of the lines should be the same style... no pull-up resistors
    - all digital I/O are +3.3V to/from FPGA
- power
    - pins [17, 18, 19, 20] are [+12V, - 12V, +5V, +3.3V]
    - pins {21, 22, 23, 24} are power ground

- review likely power supply requirements.... here are ICs identified so far
- HMC1197 :: mixer and VCO :: +3.3V (320 mA) and +5V (48 mA) 
- HMC830 or HMC833:: fractional PLL with VCO :: +3.3V (320 mA) 
- ERA-4XSM+ :: Broadband amplifier, DC-4 GHz, ultra low phase noise :: +5V (85 mA) 
- HMC542BLP4E :: digital attenuator :: +5V (3 mA) 
- CSWA2-63DR+ :: RF switch :: +5V (74 mA) 
- JSW2-63DR+ :: RF switch :: +5V (37 uA)
- ADL5375 IQ :: modulator :: +5V (200 mA)

- questions
    - [ ] What is max current for each power rail? 
    - [ ] What is noise spec for analog power rails?

jordens, 2016-10-05:
* The `IO*` numbering seems to be a bit weird but I'll attribute that to the connector.
* Do we (can we) ship (4+4)*16 digital lines over from the AMC?

gkasprow, 2016-10-05:
It's just rough idea, we can change it.
It will be difficult for all IOs, but we can use extenders for some of them
in case of troubles

dhslichter, 2016-10-06:
- ERA-4XSM amplifiers require a low-noise supply of at least ~7V; the bias current is set with an external high-power resistor.  This supply needs to be as low-noise as possible because supply fluctuations appear directly on the output, with very little supply rejection.  See datasheet, page 3: https://www.minicircuits.com/pdfs/ERA-4XSM+.pdf .  Ideally one would use an ultralow-noise LDO from +12V to generate the supply voltage.  This means we do need to be a bit careful about noise on +12V rail, in particular the frequency content of the noise.
- Typical low-speed (~ few-ish MHz) analog inputs will likely want to use instrumentation amplifiers where the input signal range is +/- 10V, thus supply voltages of +/-12V would be required.  Tom Harty will have strong feelings on this count.  These supply voltages will need to be low noise as well.  

Given these considerations, I think it makes sense to generate a reasonably low-noise +/- 12V on the RTM (heavily filtered switching regulator probably OK) and pass both rails to the daughtercards.  Since we have +/-7 V already, this would only be used for amps requiring the higher voltage.  I worry about putting switching regulators on the analog daughtercards to generate +/-12V as needed from +/- 7V, both in terms of daughtercard real estate and signal integrity due to interference from switching regulators.  

What are the 4 ADC channels on the schematic?  

@jordens the original notion for the digital lines to the analog daughtercards would be to use SERDES chips to convert slow parallel digital busses on AMC and RTM to high-speed differential to send through the AMC/RTM connector.  We did the math and figured it the connector would support it; @jbqubit has the details, I can't find them at present.

dhslichter, 2016-10-06:
If bidirectionality is desired for some DIO pins (this may or may not be the case), we can use additional serdes chip pairs (e.g. http://www.ti.com/product/DS92LV3241) to transmit input data to the AMC card via RTM.  My feeling is that we are unlikely to need bidirectionality for all channels; it might suffice to have e.g. 4 input-capable channels per daughtercard rather than 16.

dhslichter, 2016-10-06:
Also there appear to be 17 DIO on the schematic shown, not 16?

gkasprow, 2016-10-06:
The idea was to have the payload 12V for conversion purposes for users who
want +/-10 or +/-12V.
The +/-7VA can be used directly, after low pass filter or LDO to supply low
noise stuff.
The problem with +/-12V and required current consumption is the power
budget.
Let's assume we want to have +/- 12V at 1A, this already gives 24W,
multiplied by 4 mezzanines + add power conversion efficiency and you will
easily end up with >100W per RTM. This is a lot of power
From our experience with RF stuff, I can say that +/-7 is the most
universal approach.
IF you want +/-12V, just take existing 12V and invert it with capacitive
charge pump that generates very little noise. You can do it on board.

The ADC channels are for slow 24bit ADC for calibration purposes. It was
discussed in another issue.

dhslichter, 2016-10-06:
Where are you getting this 1A number for +/- 12V?  If the mezzanines are only using +/- 12V for special amp stages (and not just as a general power rail to be used to make +5 and +3.3 for the modulators/attenuators/etc), then you're talking about 2x ERA-4XSM @ 85 mA each (for example), or considerably less for instrumentation amplifier input stages.  That's more like 2W per mezzanine (8 W per RTM), much less than the 100W you are talking about.  

My points really are:
- the +12V rail needs to be low noise -- it can't be some garbage switching supply rail
- it would be nice to have a -12V rail supplied by the RTM to reduce the amount of power supply generation required on the daughtercard.  I recognize that one can do a charge pump circuit onboard to invert the voltage, but since we have extra pins on the DC connector, why not do it on the Sayma and simplify/cut noise on the daughtercard?
- the power dissipation argument is irrelevant if we also have the +/- 7VDC rails; if there is a component on the daughtercard that needs X amps at Y volts, that power is going to be dissipated no matter how you supply it, all we want to do is ensure that as little EXTRA power is dissipated by voltage regulators as possible.  As long as you are only running things that really need +12V or -12V off the +/-12V rails, it won't many any difference to your power dissipation.
- neither of these supply rails need to put out much current -- 200 mA per daughtercard would be more than enough for +12V, and the -12V rail could be ~50 mA per daughtercard.  At those ratings we're only talking 12W dissipation total.

Ack on the 24 bit ADC, I forgot about that.

dhslichter, 2016-10-06:
Related to my comment on #9, I think we should pick two pins **in addition** to the 16 pins of GPIO shown here to be dedicated to I2C (SDA/SCL).  I think we should leave the 16 GPIO pins as bidirectional fast (50 MHz) 3.3V LVCMOS lines.  We can make a recommendation for use for which pins to use for SPI, as a convention, if an SPI bus is desired.

gkasprow, 2016-10-07:
This situation would be with initial idea of just +/-12V and 5V supply where low noise 5V or 7V would be generated from +12V. If we implement both +/- 12V (100mA), +/- 7V  and 3.3V this issue then is solved

jbqubit, 2016-10-07:
[image]

dhslichter, 2016-10-07:
Suggested LDO for use on mezzanine cards:
http://www.analog.com/media/en/technical-documentation/data-sheets/ADM7150.pdf

jbqubit, 2016-10-10:
I've summarized #12 at the top of #8. If there's no more discussion about power and pin assignments lets close this.

dhslichter, 2016-10-10:
Closing this issue, all discussion related to specifics of power/IO connectors and the signals they carry to be in #8.

closed 2016-10-10 by dhslichter

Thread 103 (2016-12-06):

sinara-hw/sinara #103: Allaki output DC blocks

dtcallcock, 2016-12-06:
100pF is used throughout.  Will give high-pass at 32MHz into 50 Ohm.  The component on the board that limits the low end of the frequency range right now is the transformer which is specced down to 4.5MHz.  The DC blocks should work down to that frequency at least.  Suggest 10nF.  [ATC 520L](http://www.atceramics.com/series.aspx?sid=37&series=520L-Series) are nice but might be overkill at $0.80ea.

sbouhabib, 2016-12-19:
I replaced with a 10 nF, I had in the lib, the question do you want to go with the 520L or just "standard" cap or other?

dtcallcock, 2016-12-19:
I think a cheaper part will be fine.  I like Murata as they [publish s-parameters](http://www.murata.com/en-us/tool/sparameter/mlcc?intcid5=com_xxx_xxx_cmn_nv_xxx).  How about GRM155R71C103KA01?  It's 10000pF ±10%, 16V, X7R 0402 (1005 Metric) and costs around a cent.  From the attached S-parameters it is <0.05dB loss from 1.3MHz to 3.4GHz.

[GRM155R71C103KA01.s2p.zip](https://github.com/m-labs/sinara/files/662409/GRM155R71C103KA01.s2p.zip)

dtcallcock, 2016-12-19:
Should also note that C34 and C35 (see #109) are 100pF.  This is less of an issue if the boards are stuffed with zero ohms here (wasn't made clear what the default config would be was in #109), as then the user can pick whatever value they like if they decide to install.

jbqubit, 2016-12-21:
From call today... specify properties of capacitors
- [ ] dielectric material: eg X7R
- [ ] tolerance
- [ ] voltage rating

dtcallcock, 2016-12-21:
> If this is a problem in the future

Given the other components in the path it'll probably be hard to tell if the cap they use has weird loss/parasitics without a test fixture.  Something like the pictured eval board but having paths with and without the cap would work. Obviously would need to use same stackup and CPW dimensions as actual mezzanine.  Using the same SMAs as the mezzanine would also allow an independent check of those.  

[image]

TBH though, this is pretty far down the list of things to be worrying about and optimizing at this stage, especially at these low frequencies.

closed 2017-01-26 by sbouhabib

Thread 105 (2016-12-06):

sinara-hw/sinara #105: sayma_RTM: ADC VREF

jbqubit, 2016-12-06:
In email discussion on 7/28 @dhslichter said. "The AD9656 should have a 1.4V reference, common mode voltage of 0.9V, and can thus take 2.8 Vpp differential swings at its input.  This corresponds to VIN+=1.6, VIN-=0.2 and the reverse (i.e. each individual line can swing +/- 0.7 V around the common mode level).  Absolute maximum ratings are -0.3V and +2V for the device."

- [ ] VREF generated for AD9656 by IC2 is +1.2V, right? (p.1 of schematic). Did I miss the discussion where we moved away from 1.4V? @dhslichter 
- [ ] state the voltage of VREF on the schematic ADC_JESD204B and near IC2 (p1)
- [ ] use temperature grade A for LM4140ACM-1.2 to get 3 ppm/C

gkasprow, 2016-12-07:
@dhslichter , @jbqubit do you know good single digit ppm reference that generates 1.4V?

hartytp, 2016-12-07:
Is there any need for the reference to be that good? IIRC, it's just used for the ADC. 1LSB is 15ppm for 16 bits, and the board temp should be stable to ~1C with active fan control.

gkasprow, 2016-12-07:
That’s true, we don’t need that good one. But  it’s hard to find 1.4V reference. One can always use adjustable one or some dividers but I’d like to avoid it.

hartytp, 2016-12-07:
@gkasprow True, it's an odd voltage. Do we need to use 1.4V, or can we get away with 1.2V or something else a bit more standard? Or, use the internal reference?

gkasprow, 2016-12-08:
We can always use internal reference – the SENSE pin defines reference source. I added eternal reference to have same value for both ADCs.

We can also use internal reference of one ADC by another ADC – just remove reference source and resistor at SENSE pin of one of ADCs.

dtcallcock, 2016-12-08:
Internal reference looks to be about 45ppm/C.

If you went to a 1.25V external ref there are good options (eg MAX6070B -> 8ppm/C, 3.6uVpp noise, 0.08% accuracy, SOT23, <$0.93).  Looking at the AD9656 datasheet, it doesn't look like this would effect performance much (they spec at Vref = 1.0V and 1.4V - some things get a little better, some a little worse).  It does change the input range from 2.8Vpp to 2.5Vpp though.

> We can also use internal reference of one ADC by another ADC – just remove reference source and resistor at SENSE pin of one of ADCs.

If you do this then note the comment in the datasheet that says "If the internal reference of the AD9656 is used to drive multiple converters to improve gain matching, the loading of the reference by the other converters must be considered. Figure 52 and Figure 53 show how the internal reference voltage is affected by loading."

hartytp, 2016-12-08:
agreed, 45ppm/C for the internal reference isn't really good enough.

+1 for using a 1.25V (or other convenient voltage) external reference.

jbqubit, 2016-12-08:
@dhslichter What are implications of 1.2V vs 1.4V ?

jbqubit, 2016-12-12:
@dhslichter ping

dhslichter, 2016-12-15:
Sorry, have been on travel, very distracted.  See above from @dtcallcock -- you get smaller dynamic range for input signals, thus you degrade your SNR/ENOB/etc by this amount because the ADC input noise is in absolute voltage, not fraction of full scale.

jbqubit, 2016-12-15:
How about using +2.0 V version (LM4140ACM-2.0) and voltage divider to get +1.4V?

gkasprow, 2016-12-15:
This is what I proposed. In addition to the voltage divider, a buffer is needed. And here opamp with very low input offset must be used.

I.e. ADA4528 should do the job.

For division purposes, matched resistor pairs could be used, i.e. Vishay Y1365V0548QT9R

dtcallcock, 2016-12-15:
Comparing pages 5 and 6 of the datasheet shows that going from 1.4 to 1V gives something like a 0.1-0.2 reduction in ENOB (and actually an improvement in SFDR and harmonics).  Given we're only talking about going from 1.4 to 1.25V it doesn't seem worth adding BOM lines for.

jbqubit, 2016-12-15:
That's not much of a win. I concur with @dtcallcock. Not worth the additional materials.

gkasprow, 2017-01-12:
we leave it as it is.

closed 2017-01-12 by gkasprow

jbqubit, 2017-01-24:
@gkasprow Please confirm the following from top of this Issue.
- [ ] state the voltage of VREF on the schematic near IC2 (p1)
- [ ] use temperature grade A for LM4140ACM-1.2 to get 3 ppm/C (note on schematic)

gkasprow, 2017-01-29:
Done.
We use grade A from the very beginning.

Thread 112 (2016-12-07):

sinara-hw/sinara #112: BP_RTM/PCB_baikal schematic to git

jbqubit, 2016-12-07:
This schematic codifies several discussions including #78.

jbqubit, 2016-12-08:
@sbouhabib Please generate rough schematic for tomorrow's discussion and post here. A hand-drawn schematic should suffice.

sbouhabib, 2016-12-09:
[Baikal_rough_sch.pdf](https://github.com/m-labs/sinara/files/642357/Baikal_rough_sch.pdf)

jbqubit, 2016-12-09:
From today's conversation.
- [ ] use differential signaling for routing of clock from SMA inputs and outputs to/from 954.
- [ ] independent RF shields with removable covers for low- high-frequency distribution chains
- [ ] additional SMA output on PCB connected to 12th output of 954 for 100 MHz distribution; use is routing of 100 MHz clock to Metlino; see also #122; need to maintain clearance for 90-degree SMA 
- [ ] use nice Crystek 100 MHz TCXO as on-board reference ($20 budget)
- [ ] remove MMC
    - no use case at present for MMC on this PCB
    - [ ] use DIP switches to reconfigure clock distribution of 954's
- [ ] do we really need LTC chip for sin to square conversion on Sinara family @hartytp will make independent issue on this question
- [ ] ferite bead to decouple power

hartytp, 2016-12-10:
IIRC, for the RTMs we plan to feedback on the fan speed for each slot to provide active temperature stabilisation. Do we also plan to do this for the eRTM15? This might be a useful feature for minimising drifts in the clock phases.

jbqubit, 2016-12-12:
IIRC there are two fan speed servo's specified in uTCA.4. One common to all
AMC boards and one common to all RTM boards. Slot-to-slot air flow is
varied using static baffles.

-------
Joe Britton
Sensors and Electron Devices
Army Research Lab
2800 Powder Mill Rd
Adelphi, MD 20783
301-394-3130
joseph.w.britton5.civ@mail.mil

hartytp, 2016-12-12:
@jbqubit thanks for clarifying that.

hartytp, 2017-01-27:
@sbouhabib AFAICT, the grounds for the SMA connectors on Baikal are currently entirely floating wrt circuit ground. Are we worried about that from an ESD point of view? IIRC, on Sayma we added high resistance (100k?) pulldowns between the SMA and circuit grounds to avoid this...

jbqubit, 2017-02-13:
@sbouhabib When will this be ready for review? Please update [status](https://github.com/m-labs/sinara/wiki/status).

hartytp, 2017-04-16:
@sbouhabib ping

hartytp, 2017-08-02:
@sbouhabib Thanks for updating the designs! That all looks good to me.

jbqubit, 2017-08-03:
@sbouhabib Indeed! Thank you. :)

hartytp, 2017-08-10:
Since this has been open for a while without anyone raising any issues with the current schematic, I'm assuming that all interested parties have looked over the schematic and signed off on it. Please re-opn if that's not the case.

closed 2017-08-10 by hartytp

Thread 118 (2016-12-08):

sinara-hw/sinara #118: baikal test: RFB clock reflection due to unoccupied RTM slots

jbqubit, 2016-12-08:
First discussed in #78. 

Paraphrasing @sbouhabib
>one thing just occurred to me, the ADCLK954 has no option to turn outputs on or off, which means ,that either all outputs are on or all are off, if the whole crate is not populated, the rest are left floating which is not so nice. There may be reflections, mismatches, worse performance of ADCLK in general, higher cross-talk, unnecessary additional "noise" on the RF-backplane. 

@hartytp 
> When we have the prototype hardware, we can test whether this is actually a problem (no point complicating the circuit to fix this if it's not a problem). If the reflections do cause problems, my preferred solution would be to add an ADCLK925 (or similar) as an output buffer for each channel after the fanout buffers. These output buffers should provide sufficient isolation between the outputs.

sbourdeauducq, 2016-12-10:
@sbouhabib Why would the reflections bother the ADCLK954? We can also add termination resistors in unpopulated slots (no PCB respin, less configuration, conceptually simpler).

gkasprow, 2016-12-10:
As I said, we can use small MOSFETs with capacitor in parallel.
If you disconnect the pulldown resistor, no signal will be generated at the outuput.
Any idea why this solution would not work?

[image]

hartytp, 2016-12-10:
@gkasprow AFICT that would work fine. Would the MOSFETs be controlled from a microprocessor or using DIP switches? If we use a microprocessor, is it worth adding an RC filter on OUT_EN to ensure that noise doesn't couple onto the clock outputs?

jbqubit, 2016-12-12:
@sbourdeauducq asks "Why would the reflections bother the ADCLK954?"

The spec sheet doesn't detail output to output isolation. I think @gkasprow approach will work. Thought we agreed to use DIP switches for this type of configuration. Pads for termination resistors could be added as risk mitigation and to permit a differential test between termination vs MOSFET approach.

- [ ] add to schematic voltage supplied by OUT_EN

sbourdeauducq, 2016-12-12:
If it's DIP switches then no mosfets are needed.

sbourdeauducq, 2016-12-12:
But I'm skeptical we need any of this.

sbouhabib, 2016-12-21:
the RF backplane has pins for every slot called RF-conf which we can use as enables, this means that if a board is in the slot this output will be on using what @gkasprow suggested

sbouhabib, 2016-12-21:
the only thing left would be the 3 slots that get the CLK signals only, these cannot be controlled automatically, maybe we can leave them be, that would give us info on potential problems, while the "analog" signals throught the coax connectors are safe

jbqubit, 2016-12-21:
It's hard to talk about this without being able to see backplane schematics #135. It's new to me that RF-conf exist. I like the idea of using RF-conf by the way. :)

closed 2018-02-10 by hartytp

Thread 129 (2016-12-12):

sinara-hw/sinara #129: PCB_kasli specification

jbqubit, 2016-12-12:
@jordens is tracking design proposal/specification for Kasli on the wiki. Let's discuss PCB_kasli specification here. 

https://github.com/m-labs/sinara/wiki/Kasli

How Kasli might interface to peripherals is discussed in #99.

jbqubit, 2016-12-16:
At teleconference today we discussed freezing Kasli electrical interface so that there is compatiablity with Metlino-VHDCI #99. Did I get this right? 
- Kasli uses +12V supply to Kasli
- 8 IDC connectors on Kasli
-  each IDC connector has 
    - 16 pins for general purpose IO (eg 8 LVDS)
    - 4 pins for general purpose IO or I2C or SPI
    - +12V supply, 100 mA max
    - +5V supply, 50 mA max
- Artix-7 FGPA 

@gkasprow Which student is working on Kasli? Please add to #19 and github.

gkasprow, 2016-12-16:
I edited specification above.

dtcallcock, 2017-01-04:
@jordens Can we have subheadings for each proposed mezzanine on the wiki?

Currently the wiki mentions:
- 16 TTL drivers
- 40 DAC channels
- CameraLink connector

But some other options were mentioned in #99 including SPI interface using LVDS over RJ45 and isolated TTLs.

I would also like to suggest a low cost synthesiser for driving non-critical AOMs/EOMs (ie, where you don't need deterministic phase control or sub-kHz resolution).  Would ideally also have pre-amp/switch/attenuators/filters so that only an external power amp is needed.  Could be based on the [ADF4351](http://www.analog.com/en/products/rf-microwave/pll-synth/fractional-n-plls/adf4351.html#product-overview) (an $8 synth-on-a-chip) like the [SynthNV](https://windfreaktech.com/product/rf-signal-generator-and-power-detector/) is.

jordens, 2017-01-05:
@dtcallcock sure. Do you want to edit that yourself?

dtcallcock, 2017-01-12:
@jordens I have had a go at reorganising the wiki page based on these discussion threads and the work done so far by @gkasprow and @marmeladapk.  You guys should fill in any blanks and correct where I've misunderstood what you're up to.  I'm also a little unsure when exactly we put things on the wiki.  Do we do it right away and then discuss in the issue or suggest in the issue and move to the wiki one we've reached some kind of consensus?

I also have a few questions:

- The /ARTIQ_ALTIUM/PCB_3U_BNC folder contains two .pdf output files, one a few weeks older than the other.  Is this a mistake?

- What voltages go over the IDC?  Some schematics have +5V and some have +3.3/+12V.  Also what are the current specs?

- What is the 5th RJ45 on 3U_RJ45 going to be used for?

- Can we use thread-lock barrel connectors on the boards?  These are much more robust in a lab setting and are backwards-compatible with non-locking plugs for those that don't care.  Example parts are [connector](http://www.digikey.com/products/en?keywords=sc1472-nd) and [plug](http://www.digikey.com/product-detail/en/switchcraft-inc/761K/SC1148-ND/241919).

- Should the barrel connector input on PCB_3U_VHDCI_Baseboard have some minimal EMI filtering?

gkasprow, 2017-01-12:
I deleted wrong pdf file.
We use 12V and 3.3 for EEPROM readout. It is available even when the box is not powered.
The fifth R45 was meant as I2C link for slow devices, but I don't have strong opinion about it.
Yes, we can use such connectors. Just add an issue for Michal.
We can install CMC and EMI filter but such should be already in the power supply.

dtcallcock, 2017-01-12:
> We can install CMC and EMI filter but such should be already in the power supply.

The power supply was originally required to be "just some random wall wart".  In my experience these are often horrifically noisy and have poor regulation.  Should we add circuitry to deal with that or just change the spec to "reasonably clean isolated +12V supply".

>The fifth R45 was meant as I2C link for slow devices, but I don't have strong opinion about it.

I'd probably rather leave this off due to I2Cs lack of robustness to bus capacitance changes.  SPI will be more better for off-board devices.  If remote I2C devices are really desired though, we could utilise bus buffers like the [PCA9600](http://www.nxp.com/products/interfaces/ic-bus-portfolio/ic-voltage-level-translators/dual-bidirectional-bus-buffer:PCA9600).

There is also a high likelihood of accidentally plugging in one of the adjacent LVDS cables or vice-versa, though this could be avoided by using a different connector. 

> I deleted wrong pdf file.

The .pdf there now is the one that still has the old 5V power rail.

gkasprow, 2017-01-13:
Indeed, there is wrong schematic version still with 5V bus.

gkasprow, 2017-01-13:
fixed

jordens, 2017-01-23:
@dtcallcock looks good. Thanks! I am all on board with the additions/changes and have added a few details.

* I am okay with saying "reasonably clean 12V". But IME there are plenty of examples where standard wall wart supplies have been without problems. E.g. in the USRP. I think we can aim to replicate that.
* Supply-wise I don't care. Grep should probably choose what's best/easiest.
* The thread lock barrel connectors (or similar Bajonett style things) are a good idea.

hartytp, 2017-01-23:
Just to check: the current plan is that each Kasili communicates with/receives time from the root Metlino via a fibre link (one fibre per Kasili), and not via a backplane, right?

jordens, 2017-01-23:
Yes. The VCO/DDS synthesizer extensions would receive their reference clock individually.

Another issue is experiments where the set of Kasli extensions is sufficient. In those experiments Metlino (plus Rack, clock RTM) seems pointless and too powerful/big and requiring a separate box/piece of hardware just to be able to talk to Kasli is troublesome.

hartytp, 2017-01-23:
> Yes

@jordens Good, that seems like the correct solution to me. IIRC, the Metlino currently has 3 SFPs, which is extensible to 7 by adding an FMC-SFP board. However, given the number of different functions currently planned for Kasili, I can imagine using these all up pretty quickly. What's the plan for extending this further?

> The VCO/DDS synthesizer extensions would receive their reference clock individually.

Sure, if that's useful, although IMO it's a bit overkill: IIRC, the recovered clock should actually be pretty good noise-wise and, I assume that one be better off use Sayma for any ultra-low noise purposes. 

> Another issue is experiments where the set of Kasli extensions is sufficient. In those experiments Metlino (plus Rack, clock RTM) seems pointless and too powerful/big and requiring a separate box/piece of hardware just to be able to talk to Kasli is troublesome.

What's your plan for this use case?

dtcallcock, 2017-01-25:
> >The VCO/DDS synthesizer extensions would receive their reference clock individually.

> Sure, if that's useful, although IMO it's a bit overkill: IIRC, the recovered clock should actually be pretty good noise-wise and, I assume that one be better off use Sayma for any ultra-low noise purposes.

I can see how you might want this as an option for a DDS.  For the synth though, can the Kasli FPGA just provide the clock over one of the LVDS pairs?  I'm not entirely sure what the Artix clock output capabilities are though.

jordens, 2017-01-25:
* You get a bunch of SFPs with each Sayma. You can also hook up another (slave) Metlino to the (master) Metlino. And we can daisy chain Kaslis ad infinitum. All those require DRTIO switch support and consensus about one preferred option that would be implemented.
* Distributing the clock from Kasli to the extension boards is tricky. There is little space on the frontpanel, doing it inside makes assembly even harder than it is now (now you already have to disassemble the crate when you change/add/remove extensions), and there is little space on the PCB for SMA connectors.
* I would be afraid to run a reference clock over uncontrolled impedance, unshielded, IDC connectors, even for a simple Synth. We would also need a clock fan-out as the Artix outputs are very noisy. I am fine with putting an XO on the extension boards as a low complexity alternative to a reference clock.

hartytp, 2017-01-25:
> You get a bunch of SFPs with each Sayma. You can also hook up another (slave) Metlino to the (master) Metlino. And we can daisy chain Kaslis ad infinitum. All those require DRTIO switch support and consensus about one preferred option that would be implemented.

Good, that works for me. Is the plan for each Kasli to have 2xSFP to allow daisy chaining then?

jordens, 2017-01-25:
Right now I don't see a different use for them.

hartytp, 2017-01-25:
> I would be afraid to run a reference clock over uncontrolled impedance, unshielded, IDC connectors, even for a simple Synth. 

Depends on what the reference clock frequency is. For, say, a 100MHz reference clock frequency, routing board-board via pin header will be fine.

IIRC, the AD9912 has a pretty decent clock multiplier (PLL w/ integrated VCO), so there's no need to supply a GHz clock directly, unless one wants to push the noise performance (in which case, the Sayma might be a better choice anyway). Otherwise, one can always use something cheap like an AD9576 to do the same job.

IMO, it'd be great if these Kasli extension boards could be used without needing an external GHz frequency source...

hartytp, 2017-01-25:
@jordens My previous post was ambiguous, I meant "Is the plan for each Kasli to have 2xsSFP (which would allow them to be daisy chained)?" Answer: "yes", so I'm happy with this plan.

hartytp, 2017-01-25:
> We would also need a clock fan-out as the Artix outputs are very noisy. 

Won't there be a spare output from the Si5324 we can use to supply the reference clock?

jordens, 2017-01-25:
Yes, there are currently two SFP cages on Kasli.
Those impedance discontinuities will give us reflections which can quickly lead to double clocking leading to the need for filters etc. I would not want to go through that again.
Yes. The SI5324 has one other output. But there are eight extension cards.

hartytp, 2017-01-25:
> Those impedance discontinuities will give us reflections which can quickly lead to double clocking leading to the need for filters etc. I would not want to go through that again.

IME, this isn't too much of an issue for clocks in the 50-100MHz range. Besides which, aren't you planning to run an SPI bus at something like 50MHz over this pin header?

IIRC, the AD9912 has a max PLL divider ratio of 66, so the reference clock can be as low as 15MHz while still running at max output frequency. I really don't see any issues with reflections at that kind of clock speed.

hartytp, 2017-01-25:
> Yes. The SI5324 has one other output. But there are eight extension cards.

Sorry, I'd misread a previous post, and was talking cross-purposes here. Of course you need a fanout buffer for this...

jordens, 2017-01-25:
SPI/I2C is typically de-glitched AFAIK (at least our SPI slave is de-glitching). And with SPI you can always go slower if it doesn't work.
And for a square clock it's not the frequency that determines the reflections. It's the edge speed and the bandwidth of the input buffer at the other end. A 15 MHz clock with the same fast edges as a 1 GHz clock from a good digital fanout will give you the same distorted edges and potential double-clocking at the (fast) input of the AD9912.
We've had this at 50 MHz over much shorter connections and better-than-IDC connectors.
I'd prefer to be able to choose between standard on-board XO and good external input.

hartytp, 2017-01-25:
> And for a square clock it's not the frequency that determines the reflections. It's the edge speed and the bandwidth of the input buffer at the other end. A 15 MHz clock with the same fast edges as [...]

Sure, but if your fundamental is low, you can use a slower fanout buffer (w/ hysteresis if necessary)/lower drive current or add some RC to reduce the edge time without causing problems. 

> I'd prefer to be able to choose between standard on-board XO and good external input.

IMO, it's nice to have absolute accuracy from a PLL without having to supply an external (SMA) reference. But, I don't feel too strongly about this.

dtcallcock, 2017-01-25:
> I am fine with putting an XO on the extension boards as a low complexity alternative to a reference clock.

A decent XO will get us <1ppm which will be fine for a >1kHz resolution synth.

> The SI5324 has one other output. But there are eight extension cards.
>Distributing the clock from Kasli to the extension boards is tricky. There is little space on the frontpanel, doing it inside makes assembly even harder than it is now (now you already have to disassemble the crate when you change/add/remove extensions), and there is little space on the PCB for SMA connectors.

Could we run that spare SI5324 output to a single SMA?  Then people can use it as their 'external reference' if they so choose.  The distribution problem (for >1 extension card) still has to be solved whether they use that or another source they provide.

dtcallcock, 2017-01-25:
Another option for clock distribution is to use the backplane.  Cards could revert to using the IDC (with no clock) if no backplane is present.  

Is there currently a plan for the backplane?  The Kasli and VHDCI carriers are currently planned to have a DIN 41612 C, 96 position connector.  This would presumably make them mechanically compatible with VME J1 backplanes.  Is the idea to somehow use those or just design a custom one?  With the 96-position connector it would be trivial to wire the equivalent payload of the IDC headers (8xLVDS pairs, I2C, power) plus a clock to 4 slots in a star topology.

hartytp, 2017-01-25:
> A decent XO will get us <1ppm which will be fine for a >1kHz resolution synth.

<1ppm is pretty good for an XO -- most of the ones I've seen are more like 10ppm initial accuracy and then ~1ppm/year ageing. But, I take your point, this won't be an issue.

Another potential advantage of using an XO, rather than distributing the clock via ribbon cable, is that it makes it easier to run these extension boards off a standard microprocessor board like an Arduino.

gkasprow, 2017-01-26:
There is no standard backplane on the market, so one would have to design it.
In case of VHDCI, we would need dedicated adapter from VHDCI to the backplane.
For the moment we can just add SMA or MMCX clock output for extension boards that need it.
DO you really need to connect 8 extension  boards with clock input?
Of course we can put clock splitter at the SIlabs output to generate 8 copies of the clock.

hartytp, 2017-01-27:
@jordens When Kasli is mounted in [an enclosure](http://schroff.pentair.com/en/schroff/plug-in-units---frame-type---kits/3074457345616861429) how do you plan to bring out the ribbon cables for the daughter boards? Front panel connectors?

jordens, 2017-01-27:
@hartytp they run inside the crate between the cards. See the screenshots on the wiki page.
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

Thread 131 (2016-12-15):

sinara-hw/sinara #131: expected timeline 0.1 -> 0.2 -> 1.0

jbqubit, 2016-12-15:
In #97 @hartytp  asks

> Assuming we don't find any major mistakes in the prototype hardware, when do you think a second hardware order will take place? This will affect how much prototype hardware we buy.

- [ ] @gkasprow Please predict date when the BOM and layout will be frozen.

- [ ] @sbourdeauducq Please comment on status of ARTIQ support for Sinara hardware.

# v0.1 
From date order is placed with board house... 
    + 2 weeks for printing, stuffing (assuming 100% BOM availability)
    + 1 week for WUT PCB checks using existing test tools (no ARTIQ dependence)
    + 1 week for international shipping
    + 3 weeks for testing, thrashing, bug busting, discussions by end users and M-Labs (@jordens visits JQI for a week)
    + 2 weeks schematic update, layout fixes, repeat SI analysis 

# if v0.2
The need for a second prototype round will be decided for each PCB. From date order is placed with board house... 
    + 2 weeks for printing, stuffing 
    + 1 week for WUT PCB checks
    + 1 week for international shipping
    + 2 weeks for testing, thrashing, bug busting, discussions
    + 1 weeks schematic update, layout fixes, repeat SI analysis

# v1.0 
Design locked in... purchases are placed with board house (eg technosystem.pl)
    + 4 weeks slack for procurement spool-up by prospective customers
    + 2 weeks for printing, stuffing
    + 1 week for WUT PCB checks
    + 1 week for international shipping

If v0.1 is frozen 1/1/2017 and you believe this timeline...
    - one prototype round (v1.1) on the way to delivery of v1.0 4/7/2017
    - two prototype rounds (v0.1 -> v0.2) on the way to delivery of v1.0  6/1/2017

- [ ] @gkasprow Please comment on how realistic this progression is in your experience. 

# deprecate prototype hardware?
Depending on the type and severity of errors in prototypes it may be expedient to deprecate v0.1/v0.2 once v1.0 becomes available. If the deltas are just loop-filter components and phase-noise motivated layout tweaks I guess extended support of prototype hardware by M-Labs isn't onerous. If substantial monkeying is needed to get the prototype hardware to function at all (eg lots of flying leads, hacks to compensate for cross talk induced bit errors) deprecation may be in order. But this is speculation at this point.

sbourdeauducq, 2016-12-16:
> + 1 week for WUT PCB checks using existing test tools (no ARTIQ dependence)

@gkasprow what is your plan for the test suite?
There is also the option of keeping this initial WUT testing to a minimum (power supplies OK, check that the FPGA answers to JTAG) for v0.1, until a proper test suite is developed and used for v0.2+.

gkasprow, 2016-12-16:
@sbourdeauducq It is good idea. Wojciech is still occupied with another project so at the moment he cannot fully switch to test suite development. The plan was to at least check the SDRAM and transceivers and we should manage to do so. We can leave full connectivity checking for v0.2 when complete test suite is ready.

gkasprow, 2016-12-16:
To mitigate the risk, we can assemble only 2 pieces of Metlino/Sayma AMC to check if no critical issues are present and within a few days assemble rest of them. Initial batch count was just 2 pieces but now it grown to higher volume.
In case of serious PCB bugs we won't loose precious components but only PCBs.

sbourdeauducq, 2016-12-16:
Right now there is mostly no ARTIQ support specifically for the new hardware. We have been busy with the PDQ, SAWG and DRTIO, and https://github.com/m-labs/artiq/issues/637 has been a frustrating time sink.

The major steps for something interesting (stand-alone Sayma) are:
* Kintex Ultrascale support in OpenOCD, done using KCU105.
* GTH port of the JESD204 core, @enjoy-digital will be working on it, can be done with the KCU105.
* DDR3, not started, needs hardware to test as KCU105 uses DDR4.
* support for the RTM FPGA, not started, preferably needs hardware but KCU105 can be quite easily hooked to KC705 for testing parts of it.

jbqubit, 2016-12-16:
> To mitigate the risk, we can assemble only 2 pieces of Metlino/Sayma AMC to check if no critical issues are present

I like this approach. 

>We can leave full connectivity checking for v0.2 when complete test suite is ready.

We shouldn't migrate from v0.1 until all component connectivity is confirmed. Exception is if there's a serious bug in FGPA, SDRAM, clocking or transceivers that precludes such a check. 

>Right now there is mostly no ARTIQ support specifically for the new hardware. We have been busy with the PDQ, SAWG and DRTIO, and m-labs/artiq#637 has been a frustrating time sink.

> Wojciech is still occupied with another project so at the moment he cannot fully switch to test suite development.
> Right now there is mostly no ARTIQ support specifically for the new hardware.

Both these answers are helpful in knowing the current state of development. More is needed to answer @hartytp question. @sbourdeauducq @gkasprow Please prognosticate about the timeline for development of tools to test 
- [ ] connectivity of all PCB components 
- [ ] data integrity at full data rate
- [ ] operation of all PCB components sufficient to permit start of analog testing

gkasprow, 2016-12-16:
Production test suite and verification of connectivity are two different
things.
We can check connectivity manually, line by line and in the meantime
develop the production test suite.

jbqubit, 2016-12-16:
From today's teleconference.

@gkasprow Confirms that BOMs are frozen for all the Sinara components slated for delivery with v0.1 #97. Does this mean 

@gkasprow says to adjust timeline as follows to be conservative
* printing, stuffing (assuming 100% BOM availability): 2 weeks -> 3 weeks
* WUT PCB checks using existing test tools: 1 week -> 2 weeks

Consensus is that the following is too vague; specific tests must be defined. "3 weeks for testing, thrashing, bug busting, discussions by end users and M-Labs". Discussion goes on here #117. 

M-Labs points out that most analog tests won't be practical until @sbourdeauducq "major steps for something interesting" are accomplished. @jordens predicts 6-8 weeks from today.  

 @jordens can just as well write gateware in Germany. Delay visit to JQI until analog tests are underway. 

----------------
Updated timeline in view of today's discussion. 

# v0.1 
Assume PCB order is placed with board house 1/1/2017. 
    + 3 weeks for printing, stuffing (assuming 100% BOM availability)
    + 2 weeks for WUT PCB checks using existing test tools (no ARTIQ dependence)
        - power electronics test, DDR test, GTX transceiver test
    + 1 week for international shipping
    + 3-6 weeks for testing, thrashing, bug busting, discussions #117
        - @jordens visits JQI near the end of this interval 
        - testing depends on M-Labs' "major steps for something interesting"; available between 2/1 and 2/15
    + 2 weeks schematic update, layout fixes 

# if v0.2
The need for a second prototype round will be decided for each PCB. From date order is placed with board house... 
    + 3 weeks for printing, stuffing 
    + 1 week for WUT PCB checks (now they're rehersed)
    + 1 week for international shipping
    + 2 weeks for testing, thrashing, bug busting, discussions
    + 1 weeks schematic update, layout fixes

# v1.0 
Design locked in... purchases are placed with board house (eg technosystem.pl)
    + 4 weeks slack for procurement spool-up by prospective customers
    + 3 weeks for printing, stuffing
    + 1 week for WUT PCB checks (now routine)
    + 1 week for international shipping

jordens, 2016-12-18:
My best guess was 3-10 weeks after the tests at WUT have completed.

jmizrahi, 2017-01-10:
Can I please get an update on where the timeline stands? Has the PCB order been placed? Are these PCBs being manufactured?

gkasprow, 2017-01-10:
Hi
The Sayma-AMC board routing is finished and the layout is being verified by
Michal. Please have a look at it.
After Michal runs the SI and PI analyses I will  do the cosmetics, run net
equalisation and generate production files.
Frankly speaking I underestimated amount of work with Sayma board - it took
much longer because at some point I had to reassign almost all FPGA
connections and start routing from the beginning. Now it fits nicely on 12
layers. It took one week longer than I planned. Another problem was with
Mentor license server at the University which was closed during Xmass
period.
The China will have its New Year and all factories are closed  for 2 weeks
so we will receive the boards at the beginning of February. German company,
ILFA has 8+ week delivery time.
In case of front panels the delivery of raw bezels is 4 weeks. They say
that can make custom cutouts in 5-6 weeks.
The Sayma-RTM routing is in progress. I estimate about 10 days to have it
done.
In case of Metlino I propose to make production run after we make Sayma
running. 90% of the board is identical to Sayma and once we make Sayma AMC
running, the Metlino will work as well.
But it is up to you how we proceed.
So far all critical components (FPGAs, connectors, SFP cables) arrived.

jbqubit, 2017-01-11:
>The Sayma-AMC board routing is finished

Excellent! 

>After Michal runs the SI and PI analyses I will  do the cosmetics, run net
>equalisation and generate production files.

How long is that expected to take? 

> China will have its New Year and all factories are closed  for 2 weeks
>so we will receive the boards at the beginning of February. German company,
>ILFA has 8+ week delivery time.

I thought technosystem.pl was slated to do the PCB printing and stuffing. Right? What boards are coming from China and ILFA? 

>The Sayma-RTM routing is in progress. I estimate about 10 days to have it
>done.

OK. 

> In case of Metlino I propose to make production run after we make Sayma
> running.

Let's decide on printing of Metlino once the routing, SI and PI analyses and net equalization is done. 

> So far all critical components (FPGAs, connectors, SFP cables) arrived.

That's great news. :)

gkasprow, 2017-01-11:
@jbqubit 
Technosystem is assembly house.
PCB printing is very complex process and only a few companies are able to cope with such technology.
So we subcontract it to NCAB, ILFA, Brandner and many other companies.
We should finish PCB verification in one week.

jmizrahi, 2017-01-11:
@gkasprow I don't understand, every PCB fab house I know of can print 12 layers (or much more). Is there something driving the complexity beyond the the layer count?
Can you tell me what you think the bottom line timeline is for the first prototype to be in-hand?

gkasprow, 2017-01-11:
We use special RF material capable of 12 GHz operation. So only a few
factories can do it.
Anyway, the boards were designed for certain materials so we would have to
keep the stuckup.
So let's assume we get the boards at the beginning of February. We will
need 3..4 weeks to make them running. There is a chance that we can have it
quicker but let's be pesimistic.
We will make 2 of them running, in the meantime we will assemble remaining
boards. We will need to test them but one week should be fine.
So realistic date is middle of March.

jmizrahi, 2017-01-11:
OK, thanks for the timeline.
What is the substrate?
The 3-4 weeks to make them running includes the time to populate the components?

gkasprow, 2017-01-11:
The substrate is ISOLA FR408HR
The component assembly takes about 2-3 days and Technosystem does it.
It requires P&P programme, SMT stensil, SMT assembly, THT selective wave soldering, automatic optical inspection.
Then the boards are delivered to WUT where we verify all functionalities like power supply, mezzanines insertion, ripple measurement and optimisation, all clock circuits, SDRAM operation, GTH performance, mechanics, etc.
It really takes a while and there are always some issues to solve.

gkasprow, 2017-01-22:
Sayma RTM routing is 80% done. It is really tough, I have to do most things manually due to board packing. Sayma AMC was trivial comparing with RTM. But I will manage it.
[image]

jbqubit, 2017-01-26:
@gkasprow @sbouhabib What's status of allaki? Please update the table below so we're all on the same page. Add columns
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

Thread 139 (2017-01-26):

sinara-hw/sinara #139: m-labs Sinara timeline, checklist

jbqubit, 2017-01-26:
Similar to #131 tracking delivery timeline for Sinara hardware the intent of this Issue is to layout the steps needed for ARTIQ support of the Sinara hardware. I'm sure I'm missing items so please suggest additions. Spawn new Issues for things that require discussion. 

# phaser 
DAC gateware
- [x] jesd204b link to DAC on KC705
- [x] jesd204b dds demo [ARTIQ #580](https://github.com/m-labs/artiq/issues/580)
- [ ] two-tone demo with kc705+ad9154 [ARTIQ #561](https://github.com/m-labs/artiq/issues/561)
- [ ] DRTIO [ARTIQ #563](https://github.com/m-labs/artiq/issues/562)
    - [ ] DMA for pulse sequences [ARTIQ #553](https://github.com/m-labs/artiq/issues/553) and [ARTIQ wiki](https://github.com/m-labs/artiq/wiki/DMA)
 
# ingester (ADC gateware) 
- [ ] jesd204b input 
- [ ] jesd204b support for AD9656 
- [ ] basic servo (PID-like) [wiki](https://github.com/m-labs/sinara/wiki/Servo) 

# Sinara board support
White paper on clocking is [here](https://github.com/m-labs/sinara/wiki/SinaraClocking). ICs common to several boards in the Sinara family follow. 
- monitoring/reset/LEDs (also available for WUT via IPMI)
    - [ ] I2C_MUX
    - [ ] LM75AIMM/NOPB I2C temperature monitors
    - [ ] MAX6642ATT90 temperature sensor
- [ ] Si5324 Precision Clock Multiplier/Jitter Attenuator
- [ ] MAX24287ETK+ Ethernet interface
- [ ] FT4232H Quad High Speed USB to Multipurpose UART/MPSSE IC
- [ ] FMC support for CERN test jig used by WUT 

## Kintex Ultrascale related
This is XCKU040 FPGA. Primary tracking is [#563](https://github.com/m-labs/artiq/issues/563).
- [x] OpenOCD support for Kintex Ultrascale
- [x]  Dual flash support
- [ ]  JESD204 for Kintex Ultrascale (GTH)
- [ ]  JESD204B synchronization and group-delay/latency alignment
- [ ]  port of DRTIO to KintexUltrascale #562
- [ ]  Kintex Ultrascale DDR3
- [ ]  High-resolution IOSERDES TTLs for Kintex Ultrascale

## PCB_metlino
- LPC17762984 used for IPMI (ignored by m-labs)
- [ ] VHDCI support exposes IO that mimics Kasli peripheral interface
- [ ] RTM support exposes IO, clk in ARTIQ for future uses

## PCB_sayma_AMC
- LPC17762984 used for IPMI (ignored by m-labs)

## PCB_sayma_RTM
- [x] AD9154 DAC
- [ ] AD9656 ADC -- not yet funded
- clock distribution (summarized [here](https://github.com/m-labs/sinara/issues/75))
    - [ ] HMC7043 SPI  14-Output Fanout Buffer for JESD204B
    - [ ] HMC830 SPI fractional-N PLL
- [ ] AD7194BCPZ analog mezzanine monitoring/calibration 8-Channel, 4.8 kHz, 24-Bit ADC
- monitoring/reset/LEDs (also available for WUT via IPMI)
    - [ ] PCF8574ADW 8-Bit I/O Expander for I2C-Bus
    - [ ] 24LC64-I/MS EEPROM
- Sayma RTM/AMC FPGA link
    - [ ] XC7A15T Artix-7 FPGA
    - [ ] link support for ARTIQ SPI PHY 
        - timing requirements of remote SPI: match ARTIQ SPI PHY (what is that spec?) 
    - [ ] link support for ARTIQ TTL PHY
        - timing requirements of remote TTL: match ARTIQ TTL PHY (1 ns resolution)

## PCB_mezzanine_analog_allaki_allaki
Following is specific to Allaki and seems nearly trivial. Intent is to build infrastructure to support configuration of a variety of analog mezzanines. Assume different analog mezzanines may be installed in the same Sayma_RTM motherboard. IO is administrered by Sayma RTM/AMC FPGA link. 
- HMC542BLP4E variable attenuator via TTL PHY
- HMC849ALP4CE RF switch via TTL PHY
- AD8363ACPZ-WP readout via ADC on PCB_sayma_RTM

jbqubit, 2017-02-16:
Support needed for AD7194BCPZ analog mezzanine monitoring/calibration ADC established in Issue #141.

jbqubit, 2017-02-22:
@jordens @sbourdeauducq Please propose a road map for support of Sayma v0.1 hardware with emphasis on the LogiQ use case. Please include testing, delegation and responsibilities.

jbqubit, 2017-07-17:
M-Labs hasn't made their own roadmap or checklist for Sayma support in the ARTIQ repository. I'd like to keep this open so I can roughly track what the steps are.

sbourdeauducq, 2017-07-17:
Take our quote SINARA2 and the earlier UMD one - it's in there. Why do you want it in the ARTIQ repository?

jbqubit, 2017-07-17:
A subset of the Sayma-dependencies is funded by ARL/UMD with the balance funded by Oxford. Other groups with an interest in Sayma don't have access to the contracts that fund the gateware/software work so are unaware about what's forthcoming. My previous efforts to introspect M-Labs development plans and make lists (eg above) were not well received. Please externalize your development trajectory and priorities for the benefit of the community. A simple check list worked reasonably well for eg Sayma hardware testing #224 and got some traction with DRTIO https://github.com/m-labs/artiq/issues/562. 

> Why do you want it in the ARTIQ repository?

@jordens said in #3 "Ack. Gateware and firmware can be tracked in artiq." As a bridge between Sayma and ARTIQ consider using the ARTIQ repo sayma tag https://github.com/m-labs/artiq/labels/area%3Asayma.

hartytp, 2017-07-17:
My preferred way of handling this is to create an ARTIQ issue for each item that's funded. cf issues like [687](https://github.com/m-labs/artiq/issues/687). I'll post issues for other items we've funded (e.g. Novogorny Urukul) servo soon.

sbourdeauducq, 2017-07-17:
Yes, one issue per item sounds good. Many already exist.

jbqubit, 2017-07-17:
@hartytp I agree. One Issue per item is a good approach. @sbourdeauducq please do this for the UMD/ARL contracts. And choose a unifying tag and/or milestone.

jbqubit, 2017-07-19:
@sbourdeauducq @jordens How do you want to handle this for UMD/ARL contracts?  I'm happy to create Issues as @hartytp did but I run the risk of dictating your workflow. Please comment.

hartytp, 2017-07-24:
AFAICT, this has been done now.

closed 2017-07-24 by hartytp

jbqubit, 2017-07-24:
Yes. Thank you @sbourdeauducq and @jordens. 

4.0 mile stones -- Sayma baseline support
https://github.com/m-labs/artiq/milestone/11

5.0 mile stones -- extended Sayma support 
https://github.com/m-labs/artiq/milestone/14

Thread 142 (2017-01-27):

sinara-hw/sinara #142: Slow DAC features/specs

hartytp, 2017-01-27:
Breakout issue to discuss the Kasli/VHDCI slow DAC extension board in more detail.

The following is a combination of the info currently on the Wiki and summary of our initial thoughts on what we'd like the hardware to be able to to. All numbers are pretty rough atm:

- **Channel count**: >=30, ideally ~48
- **DAC count**: use a few lower channel-count DACs rather than a single 40ch DAC to increase update rate a bit?
- **update rate**: ~10channels simultaneously  at >=100kSPS (assume SPI running at 50MHz?)
- **Output**: +-10V (ideally +-12V using +-15V supply rails -- are these generated on the extension board using switch modes, or supplied by the carrier?)
- **Resolution**: 16 bits
- **Filters/bandwidth**: 2-pole active filter, followed by 1-pole RC. ~100kHz cut-off
- **Noise/drift**: Integrated noise/drifts (+-1C lab temperature stability) <a few LSB. Noise density above 1MHz < TBD nVrtHz 
- **Connectors**: Use cable assembly with individual screening for each channel?

jordens, 2017-01-27:
I would not focus on high update rate and not try to tweak the design for that too much. The scheduling of the individual updates over SPI is really difficult if you want to do streaming. Allocating the SPI bandwidth so that something is guaranteed is complicated.
I am fine with "fewer channels". But 32 would be my goal. You can always use more boards and leave the unused channels alone to increase the sample rate.
Yes. Connectors are a challenge. They should be easy to assemble, commonly available, mechanically and electrically good. Don't know what's en vogue nowadays. VHDCI again?
@hartytp feel free to attach labels to these issues (and make labels where missing). That simplifies searching for issues a lot.

hartytp, 2017-01-27:
> I would not focus on high update rate and not try to tweak the design for that too much. 

Agreed, optimising the bandwidth definitely shouldn't be a priority for this design. But, using a few DAC ICs rather than a single one has a minimal impact on the cost/complexity of the board and gives the user a bit more flexibility.

> The scheduling of the individual updates over SPI is really difficult if you want to do streaming. Allocating the SPI bandwidth so that something is guaranteed is complicated.

Could you elaborate on that a little, please?

jordens, 2017-01-27:
Yes. I am fine with splitting the extension so that there are as many SPI buses (plus LDAC) as we can fit on the IDC connector and 32 channels in total. But with 8 signals we can only do two SPI buses. And then we don't even have LDAC yet.

Well it's a shared bus. You can not set a channel at some arbitrary time because there might already be traffic for other channels at or around that time. You always have to treat them all as a block of channels if you want to pump lots of data. And you will be dealing with contention all the time.

hartytp, 2017-01-27:
- Are we happy to use a shared SPI clock for all DACs? (I am)
- Do we want to connect the DACs MISO (readback) lines to the IDC? (Otherwise, they can just go to a test header for debugging).
- I assume we don't need CS lines for the individual DACs.

In which case, we need a single shared clock line + 2 lines/DAC (MOSI + LDAC), allowing 3 DACs per board. 3 * 16channels = 48 channels, which seems like a good number to me.

jordens, 2017-01-27:
Sharing SPI clock breaks our SPI master. That's currently a no-go for us.
Trying to save pins by demoting MISO do "debugging" is a terrible idea.

hartytp, 2017-01-27:
Okay, if you feel that strongly about it then we can stick with a single DAC IC.

> Trying to save pins by demoting MISO to "debugging" is a terrible idea.

Out of curiosity, what do you plan to use the DAC's MISO for?

jordens, 2017-01-27:
Verifying that the chip is there, verifying that writes work, reading overtemperature indicator. Sure it's not much but I don't think saving a pin or two is worth it since even the occasional debugging would require building new bitstreams/runtime, and manual intervention inside the hardware.
SYNC is CS. We could share the two LDAC and the two MISO. Then two DACs fit on one IDC.

dtcallcock, 2017-01-27:
Or just use 2xIDC for 3x16ch DAC.  That still lets you run 192ch off a single Kasli.

> Yes. Connectors are a challenge. They should be easy to assemble, commonly available, mechanically and electrically good. Don't know what's en vogue nowadays. VHDCI again?

Individual screening will tricky without going to a custom assembly (like NI does for a lot of its products).  One simple option would be HDMI - that gets you 4 individually screened pairs in a cheap, easily available cable.  The 6 connectors needed would fit comfortably on the panel (also mini connectors are available).  Reasonable breakouts already exist: https://www.adafruit.com/products/3120

dtcallcock, 2017-01-27:
>Output: +-10V (ideally +-12V using +-15V supply rails -- are these generated on the extension board using switch modes, or supplied by the carrier?)

The carrier only provides +12V.

gkasprow, 2017-01-27:
> The carrier only provides +12V.
>
>
> yes, because most extension boards require single voltage.
On DAC ones we will add simple DC/DC converter that would produce +/-15V

gkasprow, 2017-01-27:
VHDCI are difficult to solder. Usual DB or high density DB are much more common.

hartytp, 2017-01-28:
@jordens 
> Yes. Connectors are a challenge. 

Every time we build this kind of thing, we end up going for a standard D-sub and saying "next time we should really find a better solution".

> They should be easy to assemble, commonly available, mechanically and electrically good

I'd add to that list that pre-made connectors should be available commercially with a "sensible" lead time/cost (I don't want to waste time because one of us cross-wired 2 channels for a 200 electrode ion trap when they hand assembled the cabling).

@dtcallcock 
>  One simple option would be HDMI - that gets you 4 individually screened pairs in a cheap, easily available cable. 

From an electrical perspective, HDMI is pretty nice. But, for routing say 200 channels to a trap, the cabling gets to be a bit of a mess (although, not unworkable). Also, since our signals will be single-ended, routing them as screened pairs is not ideal.

> Individual screening will tricky without going to a custom assembly (like NI does for a lot of its products). 

AFAICT, none of the cables that NI offers as stock would be suitable for this design, which is a shame. I've never looked into getting custom cable assemblies made, so no feeling for what the costs would be. Might not be too bad if we placed a bulk order for everyone who's interested?

> Usual DB or high density DB are much more common.

And, high-quality screened (but not individually screened) Dsub cables are widely available, which is a plus.

Given the relatively low speed of this design, individual screening is probably not required to keep channel-channel cross-talk to an acceptable level for cable runs of a few m (we should make sure the cables are driven from a nice low impedance though).

So, unless anyone (@gkasprow @sbouhabib) can suggest a better alternative, let's stick with DB.

For 48 DAC channels, I'd suggest either going for 2xD25 (1 GND per cable) or, if we want a bit more grounding, for 2xD37. Any preferences?

hartytp, 2017-01-28:
> Verifying that the chip is there, verifying that writes work, reading overtemperature indicator. Sure it's not much but I don't think saving a pin or two is worth it since even the occasional debugging would require building new bitstreams/runtime, and manual intervention inside the hardware.
SYNC is CS. We could share the two LDAC and the two MISO. Then two DACs fit on one IDC.

Playing devil's advocate, while I agree that it's nice to be able to read DAC registers:
- The issue isn't "saving a pin or two", it's a choice between having independent LDACs or having a (shared) MISO 
- One can verify that the board is present + powered by reading from the EEPROM via I2C, so I'm not fussed if one can't also verify that the individual DACs are present (there is still plenty that can be wrong with the board even if the DACs are responding via SPI)
- verifying that writes work is something that should only need to be done when the initial firmware is written. 
- I can count on one hand the number of times I've ever read the overtemperature indicator etc for a DAC. IME, when the DAC outputs start playing up it's generally not due to something that can be debugged by checking registers (e.g. likely to be related to an output OpAmp etc).

I would have marginally preferred to keep the LDAC lines for the two DACs separate to give the user a bit more flexibility in how the DACs are used. However, I don't feel strongly about this, as separate LDAC lines aren't required for any of the uses I have in mind (and, in any case, these boards should be cheap enough that a user can always use more boards to get more flexibility).

@dtcallcock 
> Or just use 2xIDC for 3x16ch DAC. That still lets you run 192ch off a single Kasli.

That's definitely a possibility. But, it seems nicer to keep it to 1 IDC per extension board if possible: fewer cables to make; and, makes setting up the software configuration easier.

hartytp, 2017-01-28:
Edited top-level post to include comments so far.

jordens, 2017-01-28:
Verifying that the SPI communication with the DACs works is something we would want to do in CI all the time. There will be changes to the SPI core and the drivers. There will be changes to the other layers involed in getting data to the DACs. Continuously being able to verify that these changes don't break stuff and being able to automatically identify the faulty commit is something I value very much. In all cases I can remember where convenient readback has been omitted it turned out to be the wrong decision.

hartytp, 2017-01-28:
@jordens You raise a good point -- I'm not used to thinking in terms of CI and long-term maintainability for a project of this scale. Shared LDAC and MISO it is.

gkasprow, 2017-01-28:
We can order such cables from here 

http://www.m2cables.us.com/M2-D-Sub-9-Pin-to-SMA-Fanout-Custom-Assembly-Call-p/m2cable-assembly-212.htm

or we could stick with standard DSUB-BNC SVGA cables. Just google VGA BNC

They are low cost and high performance (200MHz) and they have standard pinout. The only drawback is 5 channels. 

And they have color marking.

On a front panel we can easily fit several DB15HD connectors

You can have them for 5$ per 2meter cable.

 

Another option are CCTV cables where DSUB1HD fans out to 8 BNC, this one looks pretty standard one

http://www.dx.com/p/vga-15pin-male-to-8-bnc-female-connectors-cable-for-cctv-blue-25cm-cable-90310#.WIzzNn80968

http://www.dx.com/p/vga-15pin-male-to-8-bnc-female-connectors-cable-for-cctv-blue-white-32cm-cable-110062#.WIzzPH80968

http://www.tradekorea.com/product/detail/P310544/VGA-to-8-bnc-cable,VGA-15Pin-Male-Breakout-Cable-to-8-BNC-Female-Cable.html

http://topcctvcable.com/index.aspx?menuid=12&type=productinfo&lanmuid=48&infoid=148&language=en

 

and costs only 4$ per piece

They are used in CCTV recorders

 

we can order higher quantity from Alibaba and distribute them among interested parties.

gkasprow, 2017-01-28:
In terms of Kasli and DACs we can use single ended lines for DAC signals. 
But in case of VHDCI breakout we have much longer pairs with strong coupling between them so single-ended signalling can be used only for slow signals, after lowpass filtering and Shmidt trigger buffer.
So each LVDS can drive 8 LVDS pairs of 16 LVTTL signals in Kasli easily.
For VHDCI breakout we can also use LVTTL but only for signals that do not need high performance, i.e. DAC selection, resets, status line providing that we still meet setup and hold time constraints. 
MISO, MOSI, CLK need to be driven by LVDS transceivers.

hartytp, 2017-01-28:
@gkasprow 
> MISO, MOSI, CLK need to be driven by LVDS transceivers.

Agreed, it makes sense for these signals to be LVDS.

Thanks for the suggestions for cables to use with the (single-ended analog) DAC outputs. However, all the cables you suggested are coaxial, with SMA/BNC on one end. Given the space constraints we have in the lab, and the fact that an experiment might require 200+ DAC channels, I think we really need something with a higher density.

In the past, I've hand-assembled cables using individually screened twisted pairs (for single-ended signals, one of the pair is GND) and DB connectors on either end. As @dtcallcock points out, this is what [NI do for their DAQ cards](http://www.ni.com/datasheet/pdf/en/ds-467). IMO ideally, we'd find a solution where people can use a standard DB cable if they don't care about cross-talk, but also specify a compatible higher quality cable for more sensitive applications...

gkasprow, 2017-01-28:
In such case one can use 3M MDR (mini delta ribbon) cables.
The cables can be soldered directly to the contacts or one can use IDC version where 2 ribbons are attached simultaneously. One can use twisted pair ribbon cables as well. Special tool is required, don't try to do it at home:)
There are shielded versions of such twisted and not twisted ribbon cables from 3M.
I used MDR50 due to space constrains, but much more popular is MDR68 used in SCSI-2. One can buy such cables in various lengths.
There are popular SCSI cables with VHDCI on one end and VHDCI on another end.
National is using VHDCI68 cables but with different diff pair assignment, but for slow analog signals it won't make any difference
So we can keep NI signal assignments like here, page 16
http://www.ni.com/datasheet/pdf/en/ds-153
or page 19
http://www.ni.com/pdf/manuals/375140a.pdf
In this way one could use National terminal boxes
http://sine.ni.com/nips/cds/view/p/lang/pl/nid/10175
It's better to keep any suitable standard than no standard at all.
Just to make it difficult to mix the connections, for analog signals let's use MDR68, for digital LVDS - VHDCI. In this way there are several options for DAC outputs:
- direct fanout with individual wires connected to MDR68 contacts
- custom made cable with IDC MDR68
- SCSI cable with 2 MDR68 connectors and custom terminal box 
- SCSI-VHDCI cable or shielded NI cable with National terminal box

hartytp, 2017-01-29:
@gkasprow Thanks for posting that. I haven't used MDR before, but they look to be exactly what I was after.
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

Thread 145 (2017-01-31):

sinara-hw/sinara #145: Kasli/3U/PCB_BNC schematic & layout review

jbqubit, 2017-01-31:
Design concept is on the [wiki](https://github.com/m-labs/sinara/wiki/Kasli). Move discussion of schematic and layout from [here](https://github.com/m-labs/sinara/issues/99#issuecomment-276042586) to this Issue. 

Changes: 
- please make a key in the corner of the schematic for the different IC functions for quick reference
    - 24AA02E48T is EEPROM
    - TPS62175DQC is voltage regulator
    - SI8651BB is 150 MBPS isolator
    - SN74BCT25245 is 25-ohm bus transceiver
- R2, R4, ... should be 50 Ohm

Comments: 
- power supply caps look good for large current draw of SN74BCT25245 
- LEDs are a nice :) 
- ground plane isolation looks good

gkasprow, 2017-01-31:
@jbqubit 
If you want to have 50Ohm termination on each input, there should be switchable termination.
The BCT series chip won't be able to drive both 50Ohm termination to GND and 50Ohm load.
I will add then MOSFET and 47Ohm termination to GND when input mode is selected

jbqubit, 2017-01-31:
The most common signal source/sink in most lab is 50 Ohm coaxial. 

A Port can source and sink much more current than Port B. Why isn't Port A outward facing?

gkasprow, 2017-01-31:
Indeed, the ports should be reversed.
Port A can deliver still TTL high level (2.1V) at 80mA of output current.
It means that load resistance cannot be lower 26.5Ohm.
So if we use 50R termination and 50Ohm load then we are in forbidden region
of TTL inputs.
The original circuit was borrowed from a module where termination was
switched and that's why it worked.
So we will switch ports and add switchable termination.

dtcallcock, 2017-01-31:
Not every digital signal in the lab one may wish to sample is capable of driving 50Ohm.  Could the switching of the termination be separate to the direction?  There are spare outputs on the PCF8574 to do this but IC1 & IC4 would have to be switched to SI8650 (5 inputs on VDD2 side) to give an extra isolated line for this control. There could be some logic that prevents both 'output' and 'terminated' being selected at the same time.  

Alternatively a jumper could be added to disable the termination.

dtcallcock, 2017-01-31:
Also, could a series termination resistor be provided?  This would be populated with 0R (or jumpered) for driving 50Ohm loads and 47R for absorbing reflections when driving high impedance loads over a long 50Ohm coax cable (the usual scenario in the lab).

gkasprow, 2017-02-01:
For termination control, I can add low cost optocoupler.

Do you want to have it individually or per 4 channels?

gkasprow, 2017-02-01:
Series termination works only if cable output is opened.

If you have some capacitive load it won’t really work well.

The driver has already 25Ohm output resistance so will dump reflections to some extend.

hartytp, 2017-02-06:
@gkasprow 

Re 3U_BNC_PCB: this board looks really nice, good job!

The only thing that concerns me a little is that there is no visual indication (e.g. front panel LED) or software read-back of the termination state. 

I can imagine this leading to a lot of confusion in the lab: an experiment will often have several graduate students working on it, who may not know much about electronics. It would be easy for two BNCs to be switched around by someone who isn't aware of the termination settings, causing confusion.

There are several options for fixing this. One possibility would be to make the terminations switch in groups of 4, and then use tri-colour LEDs on the front panel rather than the current bi-colour ones (green=out, orange=in high-Z, red=in 50R). It looks like software readback might be possible using IC28/IC11 B5/A5 (AFAICT DIR1_RD and DIR2_RD are not currently connected to anything). Software control of the termination would also be nice, but it doesn't look like there is a convenient way of doing this without adding an extra isolator, so it's probably not worth it.

What do you think?

gkasprow, 2017-02-06:
The board is in production now, so we will add this feature in next release.

We can have MOSFETs switching termination resistors and LEDs on the front panel. In this way one would know which BNC is terminated while connecting the cable. Termination readout would have any practical application?

Of course, we can add switchable termination in group of 4 with visual signalization. This would need additional isolators.

hartytp, 2017-02-06:
> The board is in production now, so we will add this feature in next release.

> We can have MOSFETs switching termination resistors and LEDs on the front panel. In this way one would know which BNC is terminated while connecting the cable. 

That sounds good.

> Termination readout would have any practical application?

No, it's not really necessary.

gkasprow, 2017-02-06:
OK, so please add it as an issue to fix:)

.  <https://github.com/notifications/beacon/AEH-vnc3-xYTu4PzqEy33PkHeQlxlqPcks5rZz-6gaJpZM4Ly9LK.gif>

hartytp, 2017-02-06:
Closing this issue, since the boards have been sent for manufacture.

closed 2017-02-06 by hartytp

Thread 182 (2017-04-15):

sinara-hw/sinara #182: 3U ADC schematics

gkasprow, 2017-04-15:
@hartytp I sketched schematics of the ADC. Please look at it. All comments are welcome.
[link](https://github.com/m-labs/sinara/blob/master/ARTIQ_ALTIUM/Kasli/3U/PCB_3U_ADC/3U_ADC.PDF)

hartytp, 2017-04-16:
Wow, you work quickly Greg!

I won't comment on the digital bits, as @jordens and @sbourdeauducq are better placed than me to do that.

Asside from the usual bits of schematic tidying (labelling filter poles, removing the out of date description of the board etc), which can be done later:

- [ ] Please can you add an RC filter between the InAmps and the ADCs. IIRC, for smaller input ranges (InAmp gain of 100 or 1k), the overall noise floor will be limited by the InAmp's white noise unless we limit the bandwidth here. I'd go for a 250kHz pole, as that should be plenty fast for our applications. Users who want more bandwidth can leave this filter 0R/NC.

- [ ] Please could you move the CMCs into the RFI filter section, and correct the filter annotations to include the extra poles due to the CMCs (these give an extra CM pole at 2pi * 1.5k * 6.5mH=61kHz, and a higher frequency DM pole due to the leakage inductance, right?).

- [ ] If there is room, please can you add an extra DIP switch to allow the input ground to be shorted to circuit ground? Since the InAmp amplifies the CM voltage before subtracting it, if we keep the grounds completely floating then even mV differences between input and circuits grounds will cause issues on the highest gain setting. If possible, adjust the LEDs to indicate both termination and ground-floating.

Other than that, looks good to me.

gkasprow, 2017-04-18:
@hartytp, the InAmp's first stage does not amplify the CM signals. Notice that the feedback loop works only for diff signals. For CM signals the gain is 1 for all gain settings. Second stage has also gain of one or so for diff signals.
The only place where shorting to ground would make sense is before the CMC.

hartytp, 2017-04-18:
> For CM signals the gain is 1 for all gain settings.

Apologies, I misremembered something from a different data sheet I'd read recently. Agreed, there is no problem here (of course).

> The only place where shorting to ground would make sense is before the CMC.

I don't see a good use-case for this, so let's leave it out (unless you have an application in mind?).

hartytp, 2017-05-02:
@gkasprow Should we add a screening can to this board as well (same as DAC)?

gkasprow, 2017-05-02:
@hartytp 
It makes sense in high-impedance circuits and where inductive components are used that can pickup external noise. Since our ADC has hi-Z input, it's worth adding such option. We don't have to install it.

hartytp, 2017-05-02:
Thanks @gkasprow!

gkasprow, 2017-05-02:
We can use same shields for ADC as well. They fit without serious board modification

hartytp, 2017-05-14:
Thanks for posting the revised ADC schematics @gkasprow. That looks really nice.

Some minor comments:

- Can you remove the "please add list of IC names" comment on the schematic. IMO, this design is simple enough that a list of IC names is not required/helpful.
- Out of curiosity, why did you go for +-15V here, and not copy the DAC voltages? I don't mind about this decision, I'm just curious.
- Can you make the power budget annotation a bit clearer, like the (very nice) one on the DAC schematic?
- Is it easy to remove the screening can to access the termination switches?

gkasprow, 2017-05-14:
@hartytp 
I think we can follow DAC voltages. I simply used same values as on a devkit.
The screening can will have openings and switches will protrude from it.

hartytp, 2017-05-14:
@gkasprow Great, that sounds good to me.

As with the DAC, let's give other users until the end of **_Monday_** to provide feedback on the design.

Thanks again for all the good work Greg.

gkasprow, 2017-05-14:
[image]

closed 2017-05-15 by hartytp

jbqubit, 2017-05-22:
@hartytp Please update the wiki to reflect the locked-in specifications for Novogorny.

hartytp, 2017-05-22:
It's on my to do list. I'll probably wait until we've finished the first prototype round incase there are any significant changes.

jordens, 2017-05-22:
Just FYI: Digital and analog concept for Novogorny look good to me.

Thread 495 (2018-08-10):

### ISSUE TITLE
XADC reference

### ISSUE THREAD

**Issue by jordens** [sinara-hw/sinara#495]
* AMC: make C221 0R
* RTM: short VREFN and VREFP to GND, DNP C546

This enables the internal reference, power supply monitoring, die temperature measuremnet, and the overtemperature shutdown. Currently the RTM FPGA die is around 72 C when in use.

**Comment by hartytp** [comment]
That's quite hot. Was that measured with a fan or without?

**Comment by jordens** [comment]
Not really that hot. Kasli is the same without forced cooling.
It's Sayma-1 in HK, I don't know what the cooling situation is. @sbourdeauducq ?

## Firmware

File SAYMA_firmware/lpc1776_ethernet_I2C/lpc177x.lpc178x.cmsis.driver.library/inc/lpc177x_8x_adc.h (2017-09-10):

/**********************************************************************
* $Id$		lpc177x_8x_adc.h			2011-06-02
*//**
* @file		lpc177x_8x_adc.h
* @brief	Contains all macro definitions and function prototypes
*			support for ADC firmware library on LPC177x_8x
* @version	1.0
* @date		02. June. 2011
* @author	NXP MCU SW Application Team
* 
* Copyright(C) 2011, NXP Semiconductor
* All rights reserved.
*
***********************************************************************
* Software that is described herein is for illustrative purposes only
* which provides customers with programming information regarding the
* products. This software is supplied "AS IS" without any warranties.
* NXP Semiconductors assumes no responsibility or liability for the
* use of the software, conveys no license or title under any patent,
* copyright, or mask work right to the product. NXP Semiconductors
* reserves the right to make changes in the software without
* notification. NXP Semiconductors also make no representation or
* warranty that such application will be suitable for the specified
* use without further testing or modification.
**********************************************************************/

/* Peripheral group ----------------------------------------------------------- */
/** @defgroup ADC ADC (Analog-to-Digital Converter)
 * @ingroup LPC177x_8xCMSIS_FwLib_Drivers
 * @{
 */

#ifndef __LPC177X_8X_ADC_H_
#define __LPC177X_8X_ADC_H_

/* Includes ------------------------------------------------------------------- */
#include "LPC177x_8x.h"
#include "lpc_types.h"


#ifdef __cplusplus
extern "C"
{
#endif

/* Private macros ------------------------------------------------------------- */
/** @defgroup ADC_Private_Macros ADC Private Macros
 * @{
 */

/* -------------------------- BIT DEFINITIONS ----------------------------------- */
/*********************************************************************//**
 * Macro defines for ADC  control register
 **********************************************************************/

/**  Selects which of the AD0.0:7 pins (channels) is (are) to be sampled and converted */
#define ADC_CR_CH_SEL(n)	((1UL << n))

/**  The APB clock (PCLK) is divided by (this value plus one)
* to produce the clock for the A/D */
#define ADC_CR_CLKDIV(n)	((n<<8))

/**  Repeated conversions A/D enable bit */
#define ADC_CR_BURST		((1UL<<16))

/**  ADC convert in power down mode; if 0, it's in power down mode; if 1, it's in normal
* operation mode */
#define ADC_CR_PDN			((1UL<<21))

/**  Start mask bits */
#define ADC_CR_START_MASK	((7UL<<24))

/**  Select Start Mode controll the AD Converter in case the Burst bit is 0 (zero) */
#define ADC_CR_START_MODE_SEL(SEL)	((SEL<<24))

/**  Start conversion now */
#define ADC_CR_START_NOW	((1UL<<24))

/**  Start conversion when the edge selected by bit 27 occurs on P2.10/EINT0 */
#define ADC_CR_START_EINT0	((2UL<<24))

/** Start conversion when the edge selected by bit 27 occurs on P1.27/CAP0.1 */
#define ADC_CR_START_CAP01	((3UL<<24))

/**  Start conversion when the edge selected by bit 27 occurs on MAT0.1 */
#define ADC_CR_START_MAT01	((4UL<<24))

/**  Start conversion when the edge selected by bit 27 occurs on MAT0.3 */
#define ADC_CR_START_MAT03	((5UL<<24))

/**  Start conversion when the edge selected by bit 27 occurs on MAT1.0 */
#define ADC_CR_START_MAT10	((6UL<<24))

/**  Start conversion when the edge selected by bit 27 occurs on MAT1.1 */
#define ADC_CR_START_MAT11	((7UL<<24))

/**  Start conversion on a falling edge on the selected CAP/MAT signal */
#define ADC_CR_EDGE			((1UL<<27))

/*********************************************************************//**
 * Macro defines for ADC Global Data register
 **********************************************************************/

/** When DONE is 1, this field contains result value of ADC conversion
* (in 12-bit value) */
#define ADC_GDR_RESULT(n)		(((n>>4)&0xFFF))

/** These bits contain the channel from which the LS bits were converted */
#define ADC_GDR_CH(n)			(((n>>24)&0x7))

/** This bits is used to mask for Channel */
#define ADC_GDR_CH_MASK			((7UL<<24))

/** This bit is 1 in burst mode if the results of one or
 * more conversions was (were) lost */
#define ADC_GDR_OVERRUN_FLAG	((1UL<<30))

/** This bit is set to 1 when an A/D conversion completes */
#define ADC_GDR_DONE_FLAG		((1UL<<31))

/*********************************************************************//**
 * Macro defines for ADC Interrupt register
 **********************************************************************/

/** These bits allow control over which A/D channels generate
 * interrupts for conversion completion */
#define ADC_INTEN_CH(n)			((1UL<<n))

/** When 1, enables the global DONE flag in ADDR to generate an interrupt */
#define ADC_INTEN_GLOBAL		((1UL<<8))

/*********************************************************************//**
 * Macro defines for ADC Data register
 **********************************************************************/

/** When DONE is 1, this field contains result value of ADC conversion */
#define ADC_DR_RESULT(n)		(((n>>4)&0xFFF))

/** These bits mirror the OVERRRUN status flags that appear in the
 * result register for each A/D channel */
#define ADC_DR_OVERRUN_FLAG		((1UL<<30))

/** This bit is set to 1 when an A/D conversion completes. It is cleared
 * when this register is read */
#define ADC_DR_DONE_FLAG		((1UL<<31))

/*********************************************************************//**
 * Macro defines for ADC Status register
**********************************************************************/

/** These bits mirror the DONE status flags that appear in the result
 * register for each A/D channel */
#define ADC_STAT_CH_DONE_FLAG(n)		((n&0xFF))

/** These bits mirror the OVERRRUN status flags that appear in the
 * result register for each A/D channel */
#define ADC_STAT_CH_OVERRUN_FLAG(n)		(((n>>8)&0xFF))

/** This bit is the A/D interrupt flag */
#define ADC_STAT_INT_FLAG				((1UL<<16))

/*********************************************************************//**
 * Macro defines for ADC Trim register
**********************************************************************/

/** Offset trim bits for ADC operation */
#define ADC_ADCOFFS(n)		(((n&0xF)<<4))

/** Written to boot code*/
#define ADC_TRIM(n)		    (((n&0xF)<<8))

/**
 * @}
 */


/* Public Types --------------------------------------------------------------- */
/** @defgroup ADC_Public_Types ADC Public Types
 * @{
 */

/*********************************************************************//**
 * @brief ADC enumeration
 **********************************************************************/

/** @brief Channel Selection */
typedef enum
{
	ADC_CHANNEL_0  = 0, /*!<  Channel 0 */
	ADC_CHANNEL_1,		/*!<  Channel 1 */
	ADC_CHANNEL_2,		/*!<  Channel 2 */
	ADC_CHANNEL_3,		/*!<  Channel 3 */
	ADC_CHANNEL_4,		/*!<  Channel 4 */
	ADC_CHANNEL_5,		/*!<  Channel 5 */
	ADC_CHANNEL_6,		/*!<  Channel 6 */
	ADC_CHANNEL_7		/*!<  Channel 7 */
}ADC_CHANNEL_SELECTION;

/** @brief Type of start option */
typedef enum
{
	ADC_START_CONTINUOUS = 0,	/*!< Continuous mode */

	ADC_START_NOW,				/*!< Start conversion now */

	ADC_START_ON_EINT0,			/*!< Start conversion when the edge selected
								 * by bit 27 occurs on P2.10/EINT0 */
	ADC_START_ON_CAP01,			/*!< Start conversion when the edge selected
								 * by bit 27 occurs on P1.27/CAP0.1 */
	ADC_START_ON_MAT01,			/*!< Start conversion when the edge selected
								 * by bit 27 occurs on MAT0.1 */
	ADC_START_ON_MAT03,			/*!< Start conversion when the edge selected
								 * by bit 27 occurs on MAT0.3 */
	ADC_START_ON_MAT10,			/*!< Start conversion when the edge selected
								  * by bit 27 occurs on MAT1.0 */
	ADC_START_ON_MAT11			/*!< Start conversion when the edge selected
								  * by bit 27 occurs on MAT1.1 */
} ADC_START_OPT;


/** @brief Type of edge when start conversion on the selected CAP/MAT signal */
typedef enum
{
	ADC_START_ON_RISING = 0,	/*!< Start conversion on a rising edge
								*on the selected CAP/MAT signal */
	ADC_START_ON_FALLING		/*!< Start conversion on a falling edge
								*on the selected CAP/MAT signal */
} ADC_START_ON_EDGE_OPT;

/** @brief* ADC type interrupt enum */
typedef enum
{
	ADC_ADINTEN0 = 0,		/*!< Interrupt channel 0 */
	ADC_ADINTEN1,			/*!< Interrupt channel 1 */
	ADC_ADINTEN2,			/*!< Interrupt channel 2 */
	ADC_ADINTEN3,			/*!< Interrupt channel 3 */
	ADC_ADINTEN4,			/*!< Interrupt channel 4 */
	ADC_ADINTEN5,			/*!< Interrupt channel 5 */
	ADC_ADINTEN6,			/*!< Interrupt channel 6 */
	ADC_ADINTEN7,			/*!< Interrupt channel 7 */
	ADC_ADGINTEN			/*!< Individual channel/global flag done generate an interrupt */
}ADC_TYPE_INT_OPT;

/** @brief ADC Data  status */
typedef enum
{
	ADC_DATA_BURST = 0,		/*Burst bit*/
	ADC_DATA_DONE		 	/*Done bit*/
}ADC_DATA_STATUS;

/**
 * @}
 */


/* Public Functions ----------------------------------------------------------- */
/** @defgroup ADC_Public_Functions ADC Public Functions
 * @{
 */
/* Init/DeInit ADC peripheral ----------------*/
void ADC_Init(LPC_ADC_TypeDef *ADCx, uint32_t rate);
void ADC_DeInit(LPC_ADC_TypeDef *ADCx);

/* Enable/Disable ADC functions --------------*/
void ADC_BurstCmd(LPC_ADC_TypeDef *ADCx, FunctionalState NewState);
void ADC_PowerdownCmd(LPC_ADC_TypeDef *ADCx, FunctionalState NewState);
void ADC_StartCmd(LPC_ADC_TypeDef *ADCx, uint8_t start_mode);
void ADC_ChannelCmd (LPC_ADC_TypeDef *ADCx, uint8_t Channel, FunctionalState NewState);

/* Configure ADC functions -------------------*/
void ADC_EdgeStartConfig(LPC_ADC_TypeDef *ADCx, uint8_t EdgeOption);
void ADC_IntConfig (LPC_ADC_TypeDef *ADCx, ADC_TYPE_INT_OPT IntType, FunctionalState NewState);

/* Get ADC information functions -------------------*/
uint16_t ADC_ChannelGetData(LPC_ADC_TypeDef *ADCx, uint8_t channel);
FlagStatus ADC_ChannelGetStatus(LPC_ADC_TypeDef *ADCx, uint8_t channel, uint32_t StatusType);
uint32_t ADC_GlobalGetData(LPC_ADC_TypeDef *ADCx);
FlagStatus	ADC_GlobalGetStatus(LPC_ADC_TypeDef *ADCx, uint32_t StatusType);

/**
 * @}
 */


#ifdef __cplusplus
}
#endif


#endif /* LPC177X_8X_ADC_H_ */

/**
 * @}
 */

/* --------------------------------- End Of File ------------------------------ */

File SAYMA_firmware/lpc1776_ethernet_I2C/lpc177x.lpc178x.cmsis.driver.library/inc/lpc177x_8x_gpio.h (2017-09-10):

/**********************************************************************
* $Id$		lpc177x_8x_gpio.h			2011-06-02
*//**
* @file		lpc177x_8x_gpio.h
* @brief	Contains all macro definitions and function prototypes
*			support for GPIO firmware library on LPC177x_8x
* @version	1.0
* @date		02. June. 2011
* @author	NXP MCU SW Application Team
* 
* Copyright(C) 2011, NXP Semiconductor
* All rights reserved.
*
***********************************************************************
* Software that is described herein is for illustrative purposes only
* which provides customers with programming information regarding the
* products. This software is supplied "AS IS" without any warranties.
* NXP Semiconductors assumes no responsibility or liability for the
* use of the software, conveys no license or title under any patent,
* copyright, or mask work right to the product. NXP Semiconductors
* reserves the right to make changes in the software without
* notification. NXP Semiconductors also make no representation or
* warranty that such application will be suitable for the specified
* use without further testing or modification.
**********************************************************************/

/* Peripheral group ----------------------------------------------------------- */
/** @defgroup GPIO	GPIO (General Purpose Input/Output)
 * @ingroup LPC177x_8xCMSIS_FwLib_Drivers
 * @{
 */

#ifndef __LPC177X_8X_GPIO_H_
#define __LPC177X_8X_GPIO_H_

/* Includes ------------------------------------------------------------------- */
#include "LPC177x_8x.h"
#include "lpc_types.h"


#ifdef __cplusplus
extern "C"
{
#endif

/* Public Macros -------------------------------------------------------------- */
/** @defgroup GPIO_Public_Macros GPIO Public Macros
 * @{
 */

#define GPIO_DIRECTION_INPUT		(0)
#define GPIO_DIRECTION_OUTPUT		(1)

/** Fast GPIO port 0 byte accessible definition */
#define GPIO0_Byte	((GPIO_Byte_TypeDef *)(LPC_GPIO0_BASE))
/** Fast GPIO port 1 byte accessible definition */
#define GPIO1_Byte	((GPIO_Byte_TypeDef *)(LPC_GPIO1_BASE))
/** Fast GPIO port 2 byte accessible definition */
#define GPIO2_Byte	((GPIO_Byte_TypeDef *)(LPC_GPIO2_BASE))
/** Fast GPIO port 3 byte accessible definition */
#define GPIO3_Byte	((GPIO_Byte_TypeDef *)(LPC_GPIO3_BASE))
/** Fast GPIO port 4 byte accessible definition */
#define GPIO4_Byte	((GPIO_Byte_TypeDef *)(LPC_GPIO4_BASE))
/** Fast GPIO port 4 byte accessible definition */
#define GPIO5_Byte	((GPIO_Byte_TypeDef *)(LPC_GPIO5_BASE))



/** Fast GPIO port 0 half-word accessible definition */
#define GPIO0_HalfWord	((GPIO_HalfWord_TypeDef *)(LPC_GPIO0_BASE))
/** Fast GPIO port 1 half-word accessible definition */
#define GPIO1_HalfWord	((GPIO_HalfWord_TypeDef *)(LPC_GPIO1_BASE))
/** Fast GPIO port 2 half-word accessible definition */
#define GPIO2_HalfWord	((GPIO_HalfWord_TypeDef *)(LPC_GPIO2_BASE))
/** Fast GPIO port 3 half-word accessible definition */
#define GPIO3_HalfWord	((GPIO_HalfWord_TypeDef *)(LPC_GPIO3_BASE))
/** Fast GPIO port 4 half-word accessible definition */
#define GPIO4_HalfWord	((GPIO_HalfWord_TypeDef *)(LPC_GPIO4_BASE))
/** Fast GPIO port 4 half-word accessible definition */
#define GPIO5_HalfWord	((GPIO_HalfWord_TypeDef *)(LPC_GPIO5_BASE))

/**
 * @}
 */

/* Public Types --------------------------------------------------------------- */
/** @defgroup GPIO_Public_Types GPIO Public Types
 * @{
 */

/**
 * @brief Fast GPIO port byte type definition
 */
typedef struct {
	__IO uint8_t FIODIR[4];		/**< FIO direction register in byte-align */
	   uint32_t RESERVED0[3];	/**< Reserved */
	__IO uint8_t FIOMASK[4];	/**< FIO mask register in byte-align */
	__IO uint8_t FIOPIN[4];		/**< FIO pin register in byte align */
	__IO uint8_t FIOSET[4];		/**< FIO set register in byte-align */
	__O  uint8_t FIOCLR[4];		/**< FIO clear register in byte-align */
} GPIO_Byte_TypeDef;
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

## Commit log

2016-11-01 moving repo from artiq-hardware added protection diodes
    [DDR3_Power_Calc.XLSM, LTMxx.xlsx, UltraScale_XPE_2016_3.xlsm]
2016-11-03 added page frames added AMC-RTM FPGA UART link fixed issues with FPGA grounding
    [UltraScale_XPE_2016_3.xlsm]
2016-11-11 added _very_ initial AFE mezzanine design in Altium Designer 16
    [ADC_channel.SchDoc, AFE_mezzanine.PcbDoc, AFE_mezzanine.PrjPCB, AFE_mezzanine.SchDoc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]
2016-11-11 schematic update for DAC testing purposes added pdf schematic
    [ADC_channel.SchDoc, DAC_channel.SchDoc]
2016-11-11 added schematic tables and logo
    [ADC_channel.SchDoc, AFE_mezzanine.DXF, AFE_mezzanine.PcbDoc, AFE_mezzanine.PrjPCB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]
2016-11-22 added clock mezzanine template
    [Clock_Mezzanine.PcbDoc, Clock_Mezzanine.SchDoc, Clock_mezzanine.PrjPCB]
2016-11-22 added 3D pdf and dxf files
    [Clock_Mezzanine.DXF, Clock_Mezzanine.PcbDoc]
2016-11-28 sayma mezzanine first schematics
    [ADC_Buffer.SchDoc, ADC_Filter.SchDoc, ADC_channel.SchDoc, Amplifier.SchDoc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]
2016-11-28 updated version with EEPROM
    [AFE_mezzanine.PcbDoc, AFE_mezzanine.PrjPCB, AFE_mezzanine.SchDoc]
2016-12-01 fixed all issues: - LDOs at power supplies, - added Metlino clocking - fixed RTM clocking - fixed RTM supplies
    [ADC_Buffer.SchDoc, ADC_Filter.SchDoc, ADC_channel.SchDoc, AFE_mezzanine.DWG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]
2016-12-03 Sinara RTM - fixed issues #95, added variants Sinara Altium - updated logo path, added RF components to the design
    [ADC_Buffer.SchDoc, ADC_Filter.SchDoc, ADC_channel.SchDoc, AFE_mezzanine.PrjPCB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]
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2016-12-05 sch.update WIP
    [ADC_Buffer.SchDoc, ADC_FE4PID.SchDoc, ADC_Filter.SchDoc, ADC_Zmatching.SchDoc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]
2016-12-06 fixed project file
    [allaki_mezzanine.PrjPCB]
2016-12-06 sch update
    [ADC_FE4PID.SchDoc, B2B_connectors .SchDoc, DAC_Zmatching.SchDoc, DAC_channel.SchDoc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]
2016-12-08 added temp sensors added power calculations added 3D models
    [power consumption.xlsx]
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2016-12-11 Added PCB_MCH_mordovia files
    [PCB_MCH_mordovia.PcbDoc, PCB_MCH_mordovia.PrjPCB, PCB_MCH_mordovia.SchDoc]
2016-12-11 added resistors for thermal testing to AFE
    [AFE_mezzanine.PcbDoc, AFE_mezzanine.SchDoc]
2016-12-11 clock mezzanine update - shifted connectors, added resistors for thermal tests
    [Clock_Mezzanine.DXF, Clock_Mezzanine.PcbDoc, Clock_Mezzanine.SchDoc]
2016-12-11 Update of 3U_BNC IO module - schematics completed
    [PCB_3U_BNC.PCBDOC, PCB_3U_BNC.PrjPCB, PCB_3U_BNC.schdoc]
2016-12-12 changed project name
    [PCB_mezzanine_clock_template.PcbDoc, PCB_mezzanine_clock_template.PrjPCB, PCB_mezzanine_clock_template.SchDoc]
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2016-12-15 Metlino VHDCI base board schematics ready for review
    [PCB_3U_VHDCI_Baseboard.PCBDOC, PCB_3U_VHDCI_Baseboard.PrjPCB, PCB_3U_VHDCI_Baseboard.schdoc]
2016-12-17 layout done, ready for review. PDF with sch+render+layers generated
    [ADC_channel.SchDoc, AFE_mezzanine.PcbDoc, AFE_mezzanine.PrjPCB, AFE_mezzanine.SchDoc]
2016-12-17 updated schematic - 12V supply
    [PCB_3U_BNC.PCBDOC, PCB_3U_BNC.schdoc]
2016-12-17 schematic update - 12V supply
    [PCB_3U_VHDCI_Baseboard.PCBDOC, PCB_3U_VHDCI_Baseboard.PrjPCB, PCB_3U_VHDCI_Baseboard.schdoc]
2016-12-17 added readout of port direction over I2C.
    [PCB_3U_BNC.PCBDOC, PCB_3U_BNC.schdoc]
2016-12-17 unified I2C design with other boards
    [PCB_3U_BNC.PCBDOC, PCB_3U_BNC.schdoc]
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2017-02-27 PCB: -logos -drc fixes -new samtec
    [B2B_connectors .SchDoc, DAC_channel.SchDoc]
2017-02-27 sheet parameters fixed, pcb overlay logo fixed
    [ADC_channel.SchDoc, B2B_connectors .SchDoc, DAC_channel.SchDoc, FP_connectors.SchDoc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]
2017-03-03 part of issues/comments Fixed RFI filter upload
    [ADC_channel.SchDoc, DAC_channel.SchDoc, FP_connectors.SchDoc, allaki_mezz_top.SchDoc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]
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2017-05-14 ready for review, fixed bug - OE connection
    [PCB_3U_SMA.PrjPCB, PCB_3U_SMA.schdoc]
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2017-07-05 added LDOs, PCB shape fixed
    [CPU.SchDoc, ETH_IFC.SchDoc, LEDs.SchDoc, PA_8CH_CTRL.PrjPcb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]
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2017-07-27 fixed DRC bugs and some issues
    [CPU.SchDoc, ETH_IFC.SchDoc, LEDs.SchDoc, Output_protection.SchDoc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]
2017-08-01 All fixes applied
    [ADC_channel.SchDoc, DAC_channel.SchDoc, PowerSupply.SchDoc, allaki_mezzanine.PrjPCB]
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2017-08-19 fixed connector pinout
    [PCB_3U_CamLink.PCBDOC, PCB_3U_CamLink.schdoc]
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2017-09-02 initial PCB layout. Several bugs fixed in schematics
    [CLK_INPUT.SchDoc, CTRL_LOGIC.SchDoc, DDS_OUT_channel.SchDoc, DDS_channel.SchDoc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]
2017-09-02 Implemented most of @hartytp issues
    [DDS_OUT_channel.SchDoc, LVDS_IFC_DDS.SchDoc, PCB_3U_DDS.PrjPCB, PCB_3U_DDS.schdoc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]
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2017-09-10 fixed #295, #277, #273, #271, #270,
    [CLK_INPUT.SchDoc, CTRL_LOGIC.SchDoc, DDS_OUT_channel.SchDoc, DDS_channel.SchDoc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]
2017-09-11 fixed #294 #276 #275 #293 #290
    [DDS_OUT_channel.SchDoc, DDS_channel.SchDoc, LVDS_IFC_DDS.SchDoc, PCB_3U_DDS.PrjPCB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]
2017-09-13 Kasli fixes Moved R9 and R13 after C5 and C14, fixes #303 Moved R51 to pullup Power Good signal, fixes #301 Fixed #300 Replaced R40, fixed #305 Fixed #302 Added clock input annotation (for #306 ) Add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
    [Bill of Materials xls-PCB_3U_Kasli(standard).xls, ClockRecovery.SchDoc, FPGA.schdoc, FPGAGTP.SchDoc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]
2017-09-17 Kasli fixes Changed position of some comments and designators - check #304 Updated power budget, fixed #297 fixed #284 Added capacitors for #303
    [BackplaneConnector.SchDoc, Bill of Materials xls-PCB_3U_Kasli(standard).xls, ClockRecovery.SchDoc, FPGA.schdoc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]
2017-09-17 fixed issues #308 #307 #294 #309
    [CLK_INPUT.SchDoc, CTRL_LOGIC.SchDoc, DDS_OUT_channel.SchDoc, DDS_channel.SchDoc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]
2017-09-17 fixed #272, reduced pdf size
    [CLK_INPUT.SchDoc, CTRL_LOGIC.SchDoc, DDS_OUT_channel.SchDoc, DDS_channel.SchDoc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]
2017-09-17 fixed #282, #312, component placement done, routing started
    [CLK_INPUT.SchDoc, CTRL_LOGIC.SchDoc, DDS_OUT_channel.SchDoc, DDS_channel.SchDoc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]
2017-09-17 #282 #312 fixed, placement done, routing started
    [DDS_OUT_channel.SchDoc, DDS_channel.SchDoc, Supply_DDS.SchDoc]
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2017-09-18 Kasli fixes Fixed #311 Changed LEDs #296 Initial components placement Initial pin swapping on FPGA
    [Bill of Materials xls-PCB_3U_Kasli(standard).xls, ClockRecovery.SchDoc, FPGA.schdoc, FPGAGTP.SchDoc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]
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2017-09-24 fixed #322, still length matching needed
    [CLK_INPUT.SchDoc, DDS_OUT_channel.SchDoc, PCB_3U_DDS.PrjPCB, PCB_3U_DDS.schdoc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]
2017-10-09 fixed #325, #322, #319, #310, #309
    [CLK_INPUT.SchDoc, CTRL_LOGIC.SchDoc, DDS_OUT_channel.SchDoc, DDS_channel.SchDoc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]
2017-10-17 Production ready - fixed #321 #278 #322
    [CLK_INPUT.SchDoc, DDS_OUT_channel.SchDoc, DDS_channel.SchDoc, PCB_3U_DDS.schdoc]
2017-10-17 fixed #336 #278 #274 #337 #335 Release candidate
    [Bill of Materials-PCB_3U_DDS(AD9910).xlsx, Bill of Materials-PCB_3U_DDS(AD9912).xlsx, CLK_INPUT.SchDoc, CTRL_LOGIC.SchDoc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]
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2017-10-26 PCB routing Fixed #331 Closed #296
    [BackplaneConnector.SchDoc, ClockRecovery.SchDoc, FPGA.schdoc, FPGAGTP.SchDoc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]
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2017-10-31 Kasli routing All extensions trace length is matched within group, closes #283 Control signals and I2C routing Removed MAX6642 since XADC serves the same purpose Implemented fixes mentioned in prevoi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
    [Bill of Materials xls-PCB_3U_Kasli(standard).xls, FPGA.schdoc, FPGAGTP.SchDoc, FPGAPower&Misc.SchDoc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]
2017-10-31 fixed #314
    [CLK_DIST.SchDoc]
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2017-11-02 Kasli - small improvements in routing for PI Added note about LVDS_0 clock input capability Changed part number of J17 and J25 (didn't change 3d model yet), fixed #345 Fixed #316
    [Bill of Materials xls-PCB_3U_Kasli(standard).xls, FPGA.schdoc, PCB_3U_Kasli.PrjPCB, PowerSupplies.SchDoc]
2017-11-05 Kasli PI improvements Pin swapping in SDRAM for PI Board annotation
    [Bill of Materials xls-PCB_3U_Kasli(standard).xls, ClockRecovery.SchDoc, FPGA_SDRAM.SchDoc, PCB_3U_Kasli.PrjPCB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]
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2017-11-14 Kasli updated power budget Fixed PDF
    [PowerSupplies.SchDoc]
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2017-11-17 fixed power sequencing
    [ADC_8CH.SchDoc, LVDS_IFCA.SchDoc, PCB_3U_ADC.schdoc, Supply.SchDoc]
2017-11-18 fixed #362 fixed #363
    [ADC_8CH.SchDoc, Input_channel.SchDoc, LVDS_IFCA.SchDoc, LVDS_IFCB.SchDoc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]
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2017-11-29 fixed #374
    [ADC_8CH.SchDoc, Input_channel.SchDoc, LVDS_IFCA.SchDoc, LVDS_IFCB.SchDoc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]
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2018-01-11 fixed #377
    [Bill of Materials-Urukul(AD9910).xlsx, Bill of Materials-Urukul(AD9912).xlsx, CTRL_LOGIC.SchDoc, LVDS_IFC_DDS.SchDoc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]
2018-01-11 fixed Tom's issues
    [Bill of Materials-PCB_3U_BNC(Murata_DCDC).xlsx, DIO-BNC.PrjPCB, DIO-BNC.schdoc, DIO-BNC_Supply.SchDoc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]
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2018-01-18 fixed cosmetic issues
    [Bill of Materials-IDC_BNC_Adapter.xlsx, Bill of Materials-IDC_HD68_Adapter.xlsx, IDC_BNC_Adapter.PCBDOC, IDC_BNC_Adapter.PrjPCB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]
2018-01-20 Kasli changes for v1.1 (only schematic changes now). There is some kind of bug with generation of PCB prints, for this commit only schematics are included in PDF. R57 changed to 300R. Added two user 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
    [BackplaneConnector.SchDoc, ClockRecovery.SchDoc, FPGA.schdoc, FPGAPower&Misc.SchDoc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]
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
